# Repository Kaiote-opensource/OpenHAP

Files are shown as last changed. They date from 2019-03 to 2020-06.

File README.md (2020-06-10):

# OpenHAP
A low cost, opensource research tool with remote measurement capability for non invasive, stationary monitoring of household air pollution.



---

OpenHAP gif
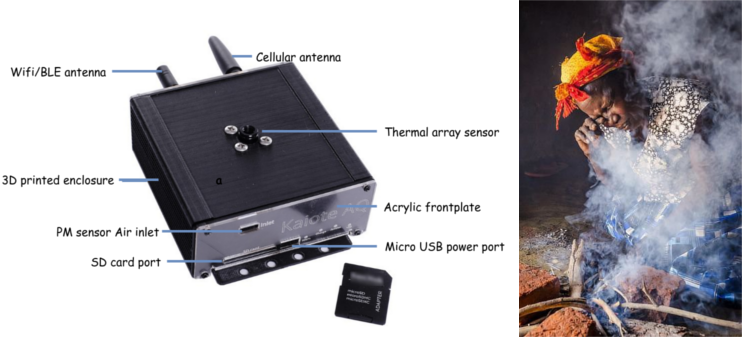
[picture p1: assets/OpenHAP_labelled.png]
OpenHAP image


General parameters monitored include: 

* **Household air pollution** using either PM 1/2.5/10 as pollution indicators.

* **Stove temperatures** in order to attribute pollution measurements above to stove characteristics while in use to answer questions such as - What phase of stove use is pollution highest for a given stove type?

* **Associated human behavioral patterns.** This is to infer behaviour that may have an indirect contribution to pollution. The device infers this by processing wireless beacons emitted by bluetooth wrist straps worn by the members of the household under study. This allows monitoring behaviour and exposure of upto 20 individuals in the same household.

OpenHAP is designed as a modular software/firmware layer that supports customizable measurement hardware. It utilises open datalogging file formats such as:

* **.csv** for timestamped measurement data.

OpenHAP gif

Figure: Sample 2D thermal image(32x24 pixels) of a human being during testing. Temperature is shown on the Z axis on the GIF. Thermal images are used to correlate stove temperature to Particulate measurements. Stove temperature can be well inferred from our tests if the stove is within the sensor's field of view. See graphical plots below from two households chosen from Kibera and rural Kenya(Kiambu).

# Sample results
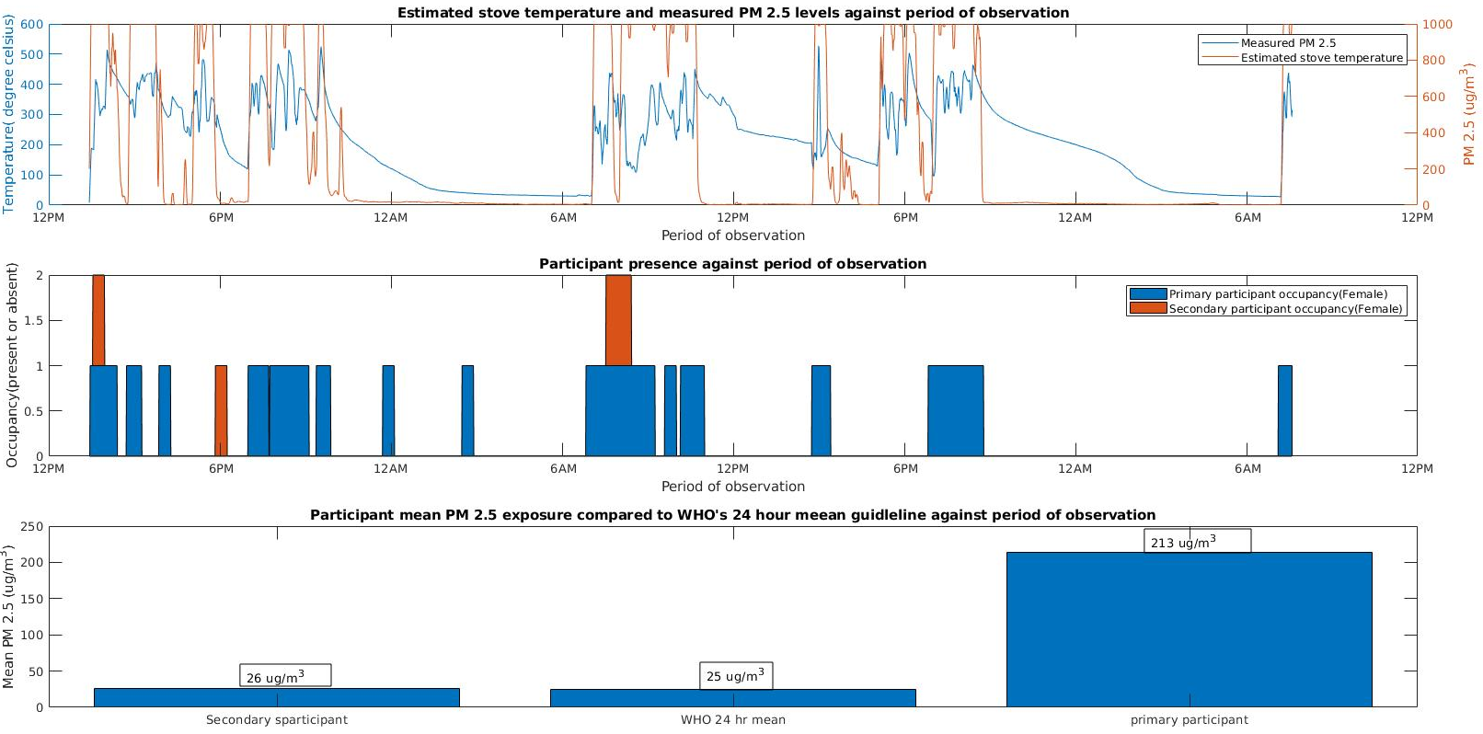
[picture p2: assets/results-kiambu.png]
OpenHAP results kiambu

Measurement results for a rural low income household,Kiambu Kenya with two middle aged women. Household energy use - Three Stone Open Fire(TSOF)

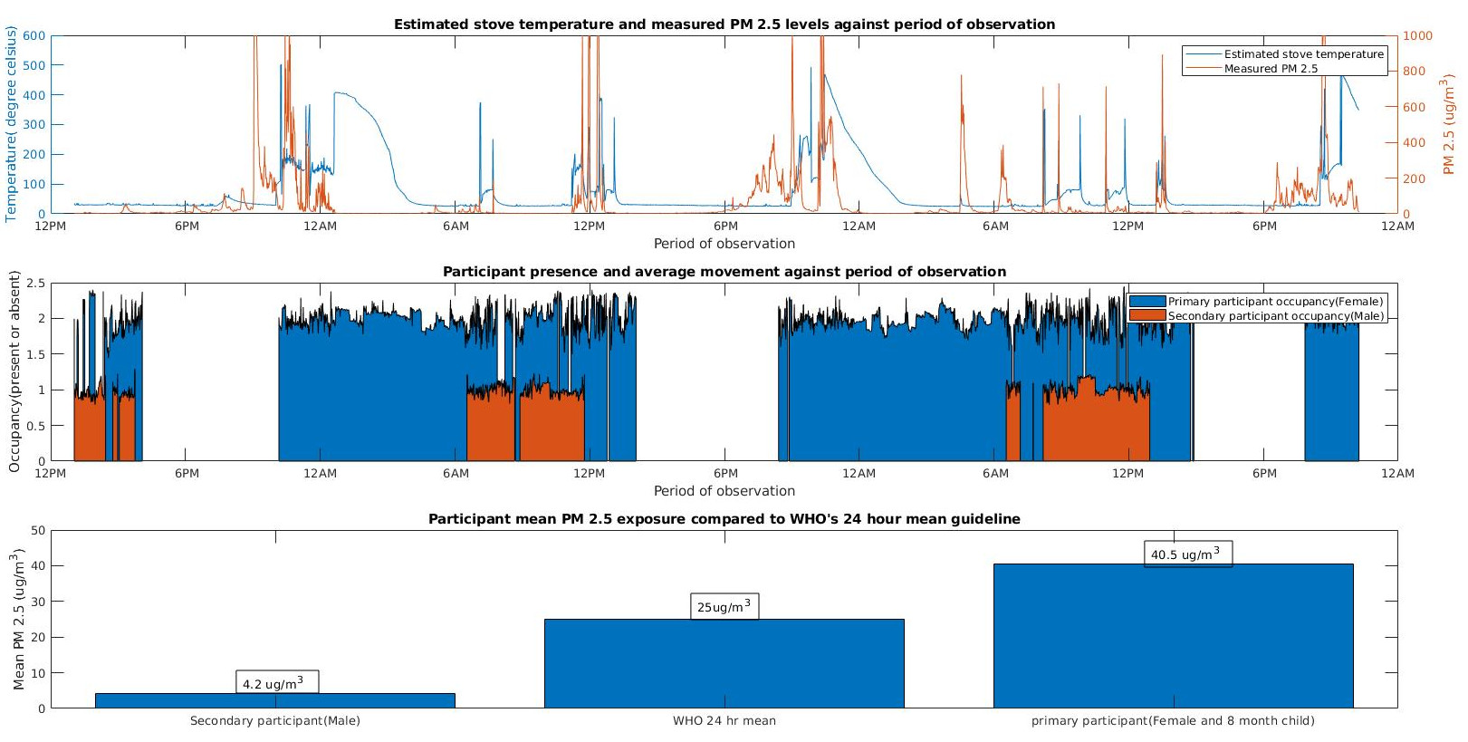
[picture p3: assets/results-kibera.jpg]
OpenHAP results kibera

Measurement results for an urban low income household,Kibera Kenya occupied by a man, wife and 2 children. Children were not monitored in our study as majority of their time was spent with the mother. Household energy use - Kerosene and charcoal briquettes.

# Documentation
OpenHAP's story is covered in [this hackaday article](https://hackaday.com/2019/09/24/fighting-household-air-pollution/) with indepth technical documentation at [this link](https://hackaday.io/project/166510-openhap)

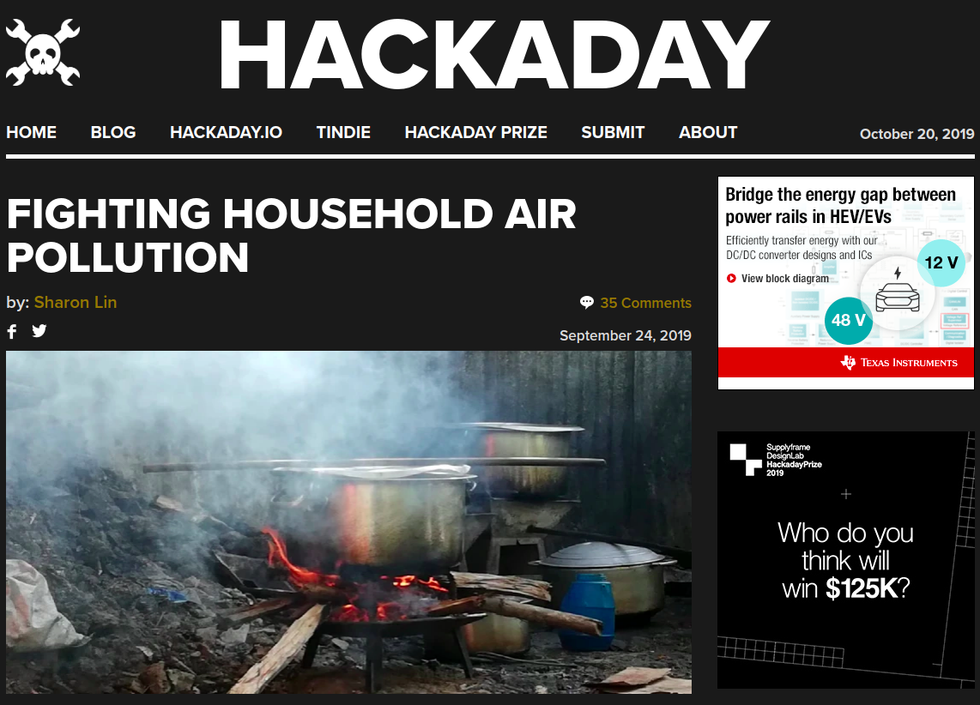
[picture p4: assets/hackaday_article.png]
OpenHAP article (https://hackaday.com/2019/09/24/fighting-household-air-pollution/)


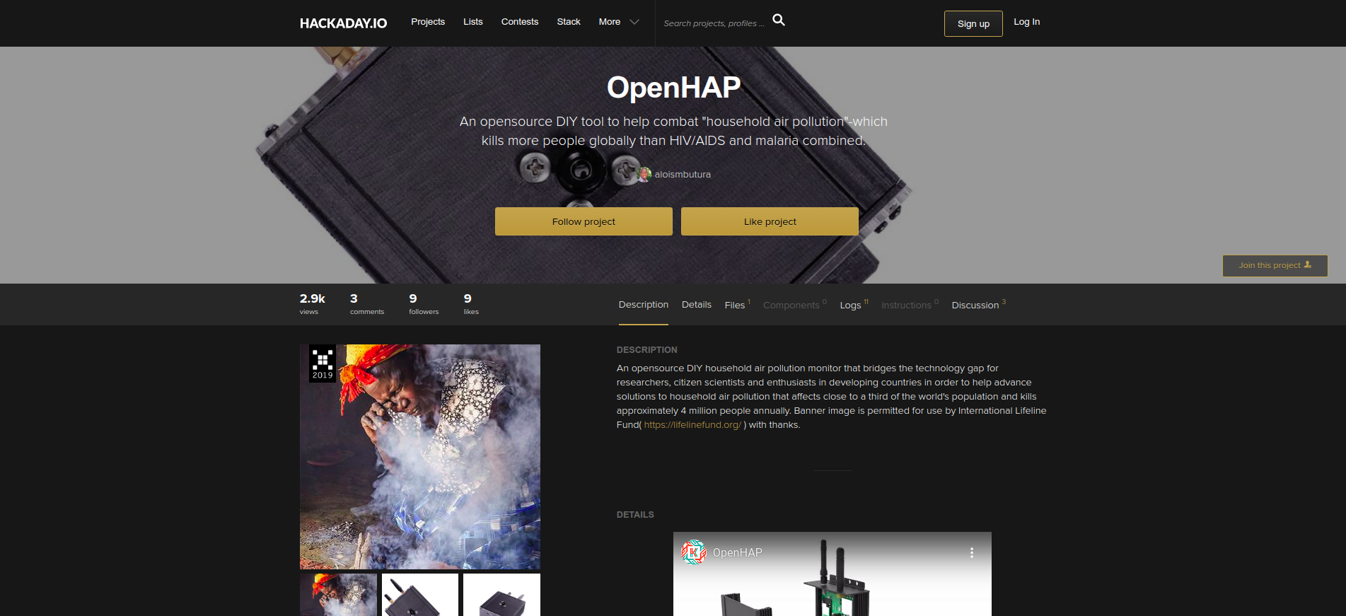
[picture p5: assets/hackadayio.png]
OpenHAP documentation (https://hackaday.io/project/166510-openhap)


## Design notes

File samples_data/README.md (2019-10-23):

# Samples

Real world data captured by OpenHAP and associated simple data analysis examples.

## CSV data fields

* **Time**- Absolute time of measurement in Unix time(Elapsed time in seconds since the unix epoch 00:00:00 UTC - 1 January 1970). A good tool to decode this non-programatically is https://www.epochconverter.com/.

* **Mean temp**- Mean of all 24x32 pixel temperatures in OpenHAP's thermal imager's field of view(FOV).

* **Max temp**- Maximum of all 24x32 pixel infared temperatures in OpenHAP's thermal imager's field of view(FOV).

* **Min temp**- Minimum of all 24x32 pixel temperatures in OpenHAP's thermal imager's field of view(FOV).

* **Temp variance**- Variance of all 24x32 pixel temperatures in OpenHAP's thermal imager's  field of view(FOV).

* **Temp variance**- square root of the Temperature variance above.

* **Humidity**- Ambient humidity at the time of measurement.

* **Temperature**- Ambient temperature at the time of measurement.

* **PM 1**- Amount of PM 1 measured within a one second interval based on the particulate matter sensor's active pump characteristics such volume of air swept per unit time.

* **PM 2.5**- Amount of PM 2.5 measured within a one second interval based on the particulate matter sensor's active pump characteristics such volume of air swept per unit time.

* **PM 10**- Amount of PM 10 measured within a one second interval based on the particulate matter sensor's active pump characteristics such volume of air swept per unit time.

* **Bluetooth tag ID_count**- Number of pings a specific bluetooth tag, identified by its MAC address, makes to an OpenHAP unit within a measurement period.

* **Bluetooth tag ID_mean_dBm**- Average signal streangth in decibel-milliWatts(dBm) of all pings received from a specific bluetooth tag, within a measurement period.

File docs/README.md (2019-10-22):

# Documentation

* **research_papers**- Open research papers on metrology, instrumentation and calibration of low cost sensors, with their citations.

* **datasheets_and_technical_references** - datasheets that guide driver development in the OpenHAP ecosystem. Only drivers of components that have been added or shall be added should have their datasheets here.

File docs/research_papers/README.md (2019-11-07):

# Citations

## Basics

* Schulze, F., Gao, X., Virzonis, D., Damiati, S., Schneider, M. R., & Kodzius, R. (2017). Air Quality Effects on Human Health and Approaches for Its Assessment through Microfluidic Chips. Genes, 8(10), 244. doi:10.3390/genes8100244

## Low cost sensors - Evaluation

* Zheng, Tongshu & Bergin, Michael & Johnson, Karoline & Tripathi, Sachchida & Shirodkar, Shilpa & Landis, Matthew & Sutaria, Ronak & Carlson, David. (2018). Field evaluation of low-cost particulate matter sensors in high- and low-concentration environments. Atmospheric Measurement Techniques. 11. 4823-4846. 10.5194/amt-11-4823-2018. 

* Aerosol Physics and Instrumentation Volume: 19 | Issue: 1 | Pages: 181-194 DOI: 10.4209/aaqr.2017.12.0611

## Ventilation measurements - Tracer Decay technique

* Clito Afonso, Tracer gas technique for measurement of air infiltration and natural ventilation: case studies and new devices for measurement of mechanical air ventilation in ducts, International Journal of Low-Carbon Technologies, Volume 10, Issue 3, September 2015, Pages 188–204, https://doi.org/10.1093/ijlct/ctt025

## Outdoor-Indoor pollution parameter correlation

* Mahmoud M. M. Abdel-Salam (2015) Investigation of PM2.5 and carbon dioxide levels in urban homes, Journal of the Air & Waste Management Association, 65:8, 930-936, DOI: 10.1080/10962247.2015.1040138

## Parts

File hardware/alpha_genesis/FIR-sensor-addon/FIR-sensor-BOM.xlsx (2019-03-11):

C1 | 0.1uF/25V(10%)/0805 | Capacitor_SMD:C_0805_2012Metric_Pad1.15x1.40mm_HandSolder | http://www.yageo.com/documents/recent/UPY-GPHC_X7R_6.3V-to-50V_18.pdf | 311-1141-1-ND | digikey | 1
C2 | 1uF/6.3v(10%)/0805 | Capacitor_SMD:C_0805_2012Metric_Pad1.15x1.40mm_HandSolder | http://www.yageo.com/documents/recent/UPY-GPHC_X7R_6.3V-to-50V_18.pdf | 311-3418-1-ND | digikey | 1
J1 | Conn_02x03_Odd_Even | Connector_PinHeader_2.54mm:PinHeader_2x03_P2.54mm_Vertical | https://cdn.amphenol-icc.com/media/wysiwyg/files/drawing/68000.pdf | 609-3263-ND | digikey | 1
U1 | MLX90640 | lib_kaiote:MLX90640 | https://www.mouser.com/datasheet/2/734/MLX90640-Datasheet-Melexis-1324357.pdf | MLX90640ESF-BAB-000-SP-ND | digikey | 1

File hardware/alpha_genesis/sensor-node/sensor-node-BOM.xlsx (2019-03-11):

Reference designator | Customer reference | Digikey part number | vendor | quantity per board
BT1 | Battery_Cell | BAT-HLD-001-ND | digikey | 1
BT2 | Battery_Cell | 455-1749-1-ND | digikey | 1
BZ1 | Buzzer | 433-1028-ND | digikey | 1
C2, C14 | 1nF/50v(10%)/0805 | 399-1147-1-ND | digikey | 2
C3 | 100uF/6.3v(20%)/1206 | 490-7217-1-ND | digikey | 1
C4 | 1uF/6.3v(10%)/0805 | 311-3418-1-ND | digikey | 1
C6 - C10 | 10uF/25V(10%)/0805 | 490-5523-1-ND | digikey | 4
C8 | 220uF/tantalum | 478-6612-1-ND | digikey | 1
C1 - C19 | 0.1uF/25V(10%)/0805 | 311-1141-1-ND | digikey | 7
C15, C16 | 4.7uF/16v/10%/0805 | CL21A475KOFNNNE | digikey | 2
C17 | 220nF/50V(10%)/0805 | 587-1287-1-ND | digikey | 1
D1, D19 | TVS_5V | SMAJ5.0ALFCT-ND | digikey | 2
D2 - D17 | D_Schottky | B120-FDICT-ND | digikey | 3
D3 - D8 | CDSOT23-T03C | CDSOT23-T03CCT-ND | digikey | 6
D9 - D16 | TVS_3V3 | SMBJ3V3-E3/52GITR-ND | digikey | 4
D11 | Red/RA | 754-1840-1-ND | digikey | 1
D13 - D24 | Green/RA | 754-1057-1-ND | digikey | 3
J1 | USB_B_Micro | WM17141CT-ND | digikey | 1
J2 | TE_2041021 | A101492CT-ND | digikey | 1
J3 | Conn_02x03_Odd_Even | 609-3263-ND | digikey | 1
J4 | Conn_01x07 | S5443-ND | digikey | 1
J5 | Conn_01x03_Male | 732-5316-ND | digikey | 1
J6 | Conn_01x08 | WM7612CT-ND | digikey | 1
Q1, Q2 | S8050 | MMSS8050-H-TPMSCT-ND | digikey | 2
Q3, Q9 | SI2323DDS-T1-GE3 | SI2323DDS-T1-GE3 | digikey | 2
Q4 - Q8 | BSS138 | BSS138CT-ND | digikey | 4
R12, R13 | 12k(1%) | A126337CT-ND | digikey | 2
R1 - R28 | 10k(5%) | 311-10KARCT-ND | digikey | 16
R15 - R29 | 10k(0.5%) | RR12P10.0KDCT-ND | digikey | 3
R18, R31 | 100k(5%) | RMCF0805FT100KCT-ND | digikey | 2
R19, R20 | 470R(5%) | P470ACT-ND | digikey | 2
R21, R22 | 2.4k(5%) | RMCF0805JT2K40CT-ND | digikey | 2
R23, R27 | 2K(5%) | RMCF0805JT2K00CT-ND | digikey | 2
R30 | 2.4k(0.1%) | P2.4KDACT-ND | digikey | 1
SW1 | ~ | EG2508-ND | digikey | 1
TP1 - TP14 | ~ | 36-5015CT-ND | digikey | 14
U1 | DS3231SN | DS3231SN#T&RCT-ND | digikey | 1
U2 | MIKROE_CLICK_GSM | 1471-1065-ND | digikey | 1
U3 | ESP32-WROVER | 1904-1017-1-ND | digikey | 1
U4 | TCA9534 | 296-40573-1-ND | digikey | 1
U5 | NCP1117-3.3_SOT223 | NCP1117ST33T3GOSCT-ND | digikey | 1
U7 | 74LVC1G3157 | 296-14908-1-ND | digikey | 1
U8 | MCP73812T-420I-OT | MCP73832T-2ACI/OTCT-ND | digikey | 1
U9 | HIH6030-021-001 | 480-5704-1-ND | digikey | 1

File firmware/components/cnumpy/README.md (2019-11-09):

# cnumpy

cnumpy is a derivative work of c2numpy by Jim Pivarski . cnumpy carries over the original Apache licence used.

cnumpy is an ANSI C compatible library that allows the ability to read and write .npy files. npz files are not supported as they use gzip compression which only supports block compression(deflate/infalte operations must have a destination buffer in RAM, limiting performance on large file operations. This would make it unable to support low ram utilisation operations.

# file format

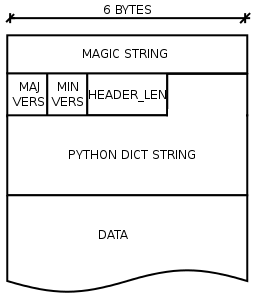
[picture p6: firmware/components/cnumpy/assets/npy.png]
npy file


The .npy file format can be found here: https://numpy.org/devdocs/reference/generated/numpy.lib.format.html

# OpenHAP application

The npy file format is useful for storing thermal image data. It may also be extended to other data types with fixed/pre-determined size.

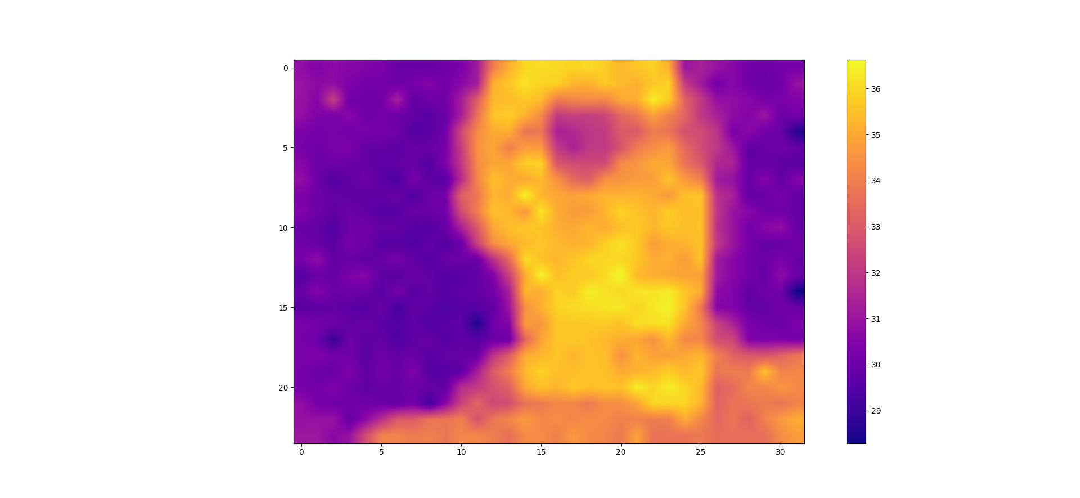
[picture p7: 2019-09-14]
firmware/components/drivers_thermal_imagers/python/Figure_1.png

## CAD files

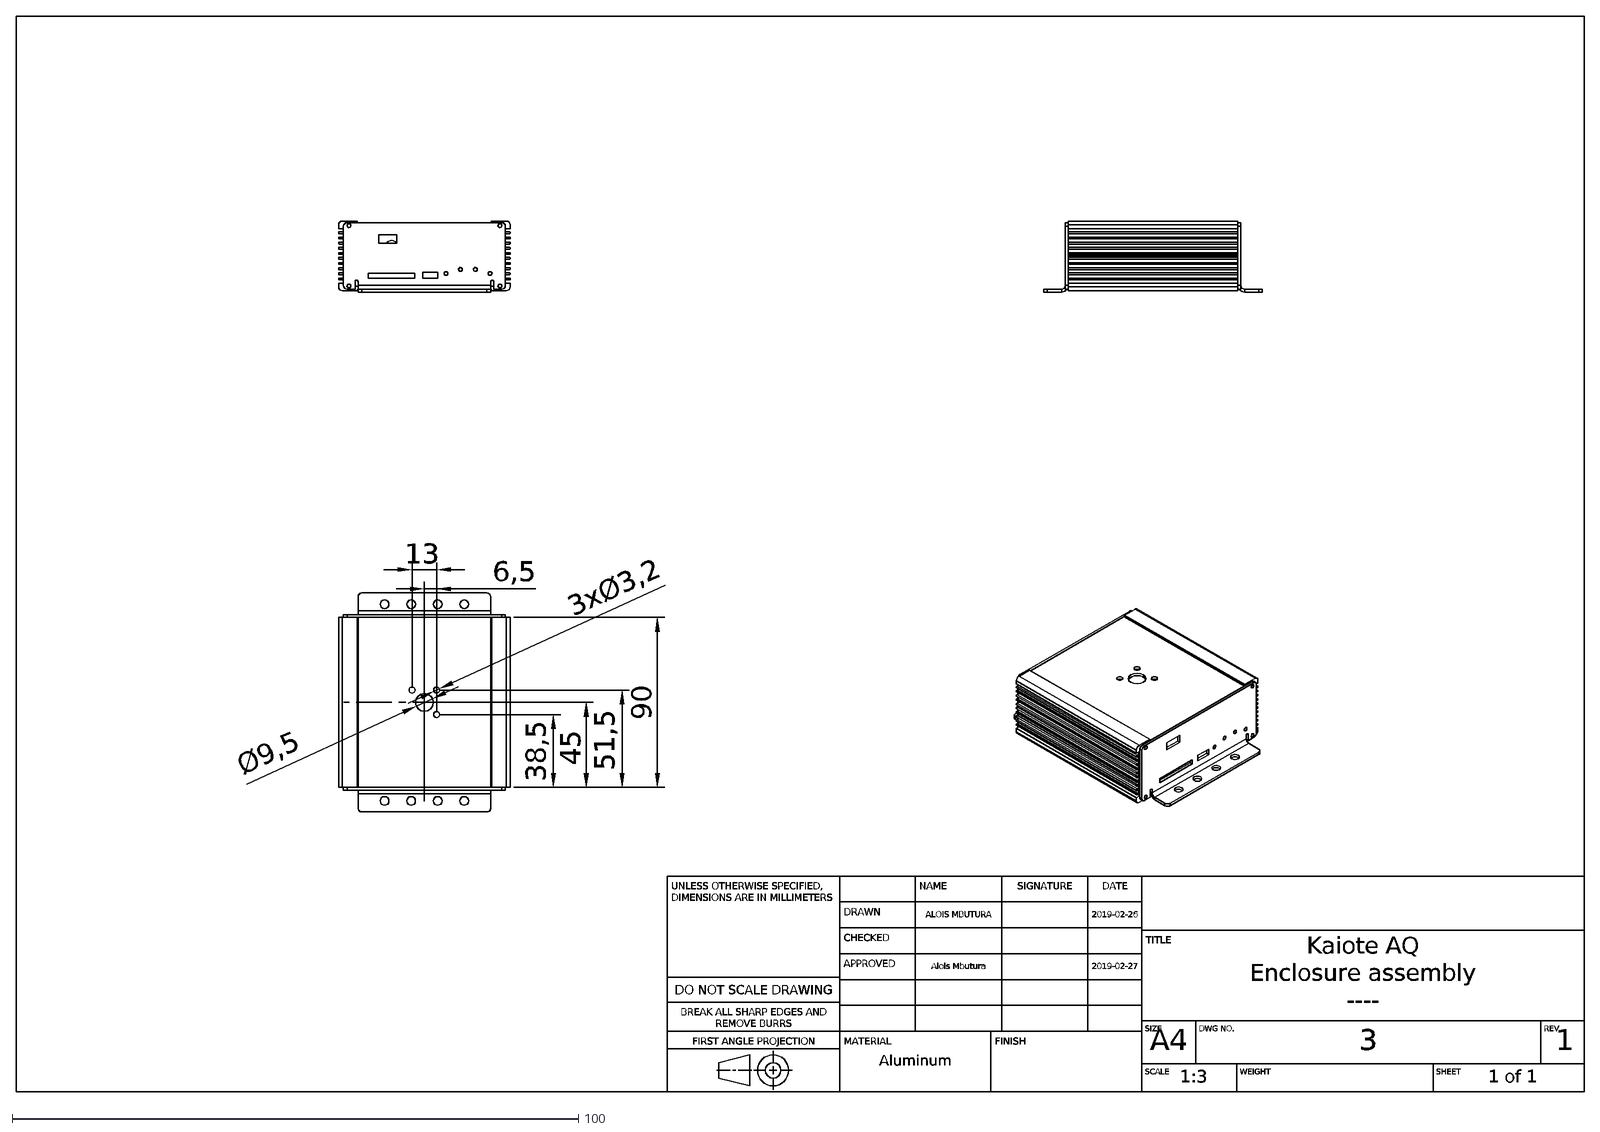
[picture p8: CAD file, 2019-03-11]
hardware/alpha_genesis/MCAD/Enclosure_instructions/Assembly/Enclosure_assembly.dxf
UNLESS OTHERWISE SPECIFIED, DIMENSIONS ARE IN MILLIMETERS
DO NOT SCALE DRAWING
BREAK ALL SHARP EDGES AND REMOVE BURRS
FIRST ANGLE PROJECTION
SIGNATURE
NAME
DATE
DRAWN
ALOIS MBUTURA
2019-02-26
CHECKED
APPROVED
Alois Mbutura
2019-02-27
MATERIAL
Aluminum
FINISH
TITLE
Kaiote AQ
Enclosure assembly
----
SIZE
A4
DWG NO.
3
REV.
1
SCALE
1:3
WEIGHT
SHEET
1 of 1
90
38,5
45
51,5
13
6,5
Ø9,5
3xØ3,2

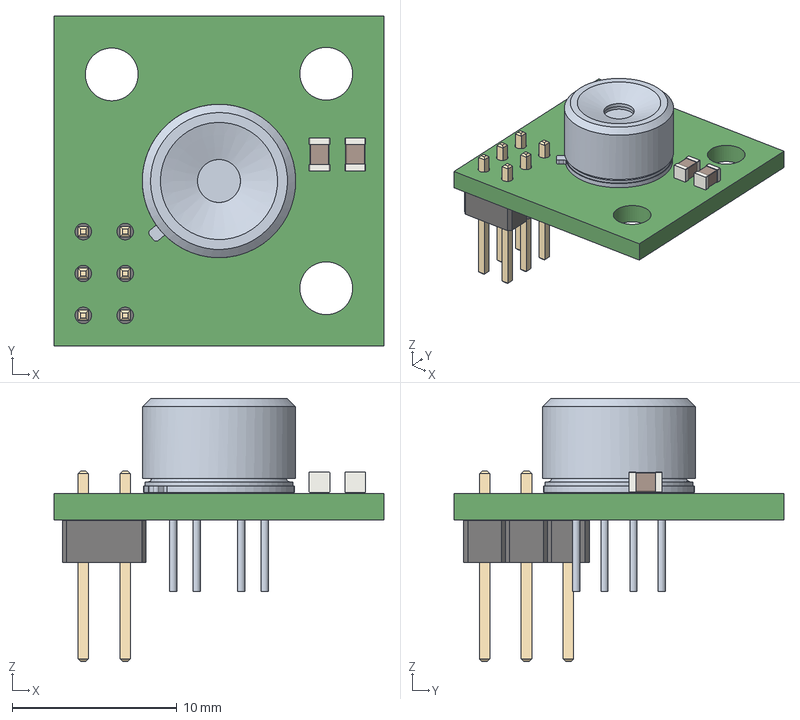
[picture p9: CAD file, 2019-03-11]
hardware/alpha_genesis/FIR-sensor-addon/FIR-sensor-addon.step
20.0 x 20.0 x 15.9 mm

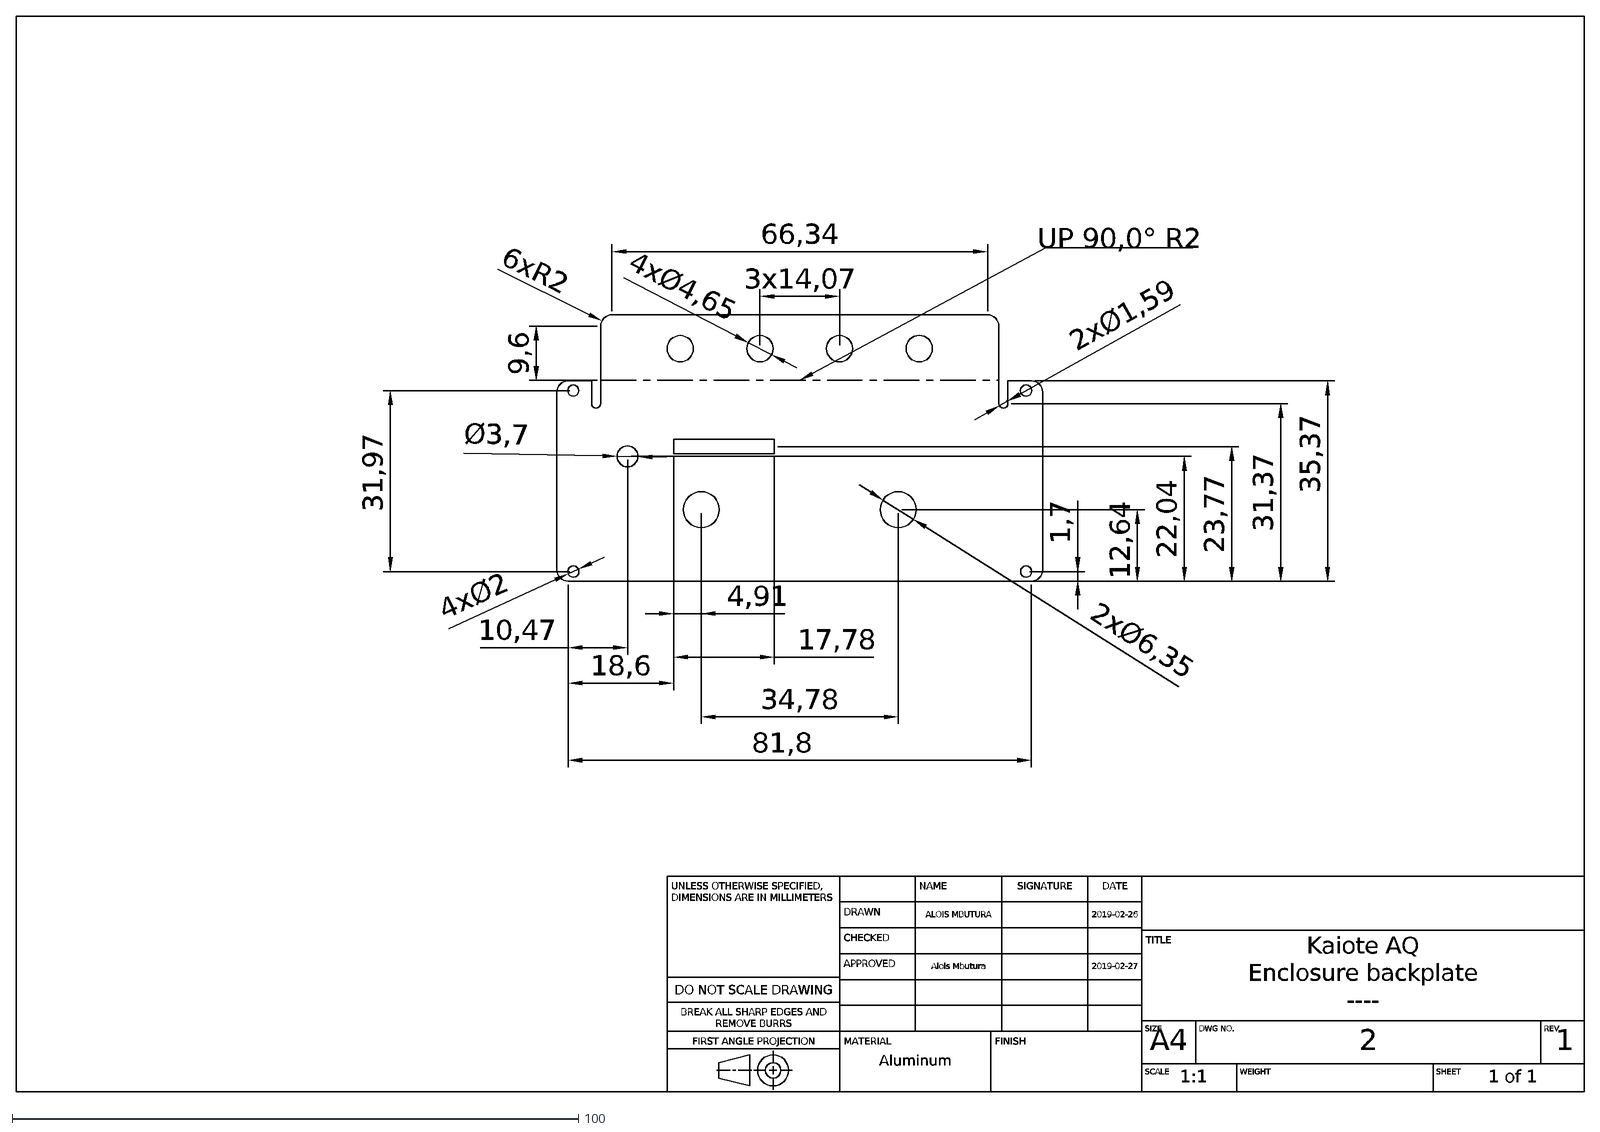
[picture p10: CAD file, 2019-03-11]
hardware/alpha_genesis/MCAD/Enclosure_instructions/backplate/Enclosure_backplate.dxf
UNLESS OTHERWISE SPECIFIED, DIMENSIONS ARE IN MILLIMETERS
DO NOT SCALE DRAWING
BREAK ALL SHARP EDGES AND REMOVE BURRS
FIRST ANGLE PROJECTION
SIGNATURE
NAME
DATE
DRAWN
ALOIS MBUTURA
2019-02-26
CHECKED
APPROVED
Alois Mbutura
2019-02-27
MATERIAL
Aluminum
FINISH
TITLE
Kaiote AQ
Enclosure backplate
----
SIZE
A4
DWG NO.
2
REV.
1
SCALE
1:1
WEIGHT
SHEET
1 of 1
4xØ2
81,8
34,78
1,7
12,64
22,04
23,77
31,37
35,37
2xØ1,59
31,97
9,6
6xR2
66,34
17,78
10,47
2xØ6,35
18,6
4,91
4xØ4,65
3x14,07
Ø3,7
UP 90,0° R2

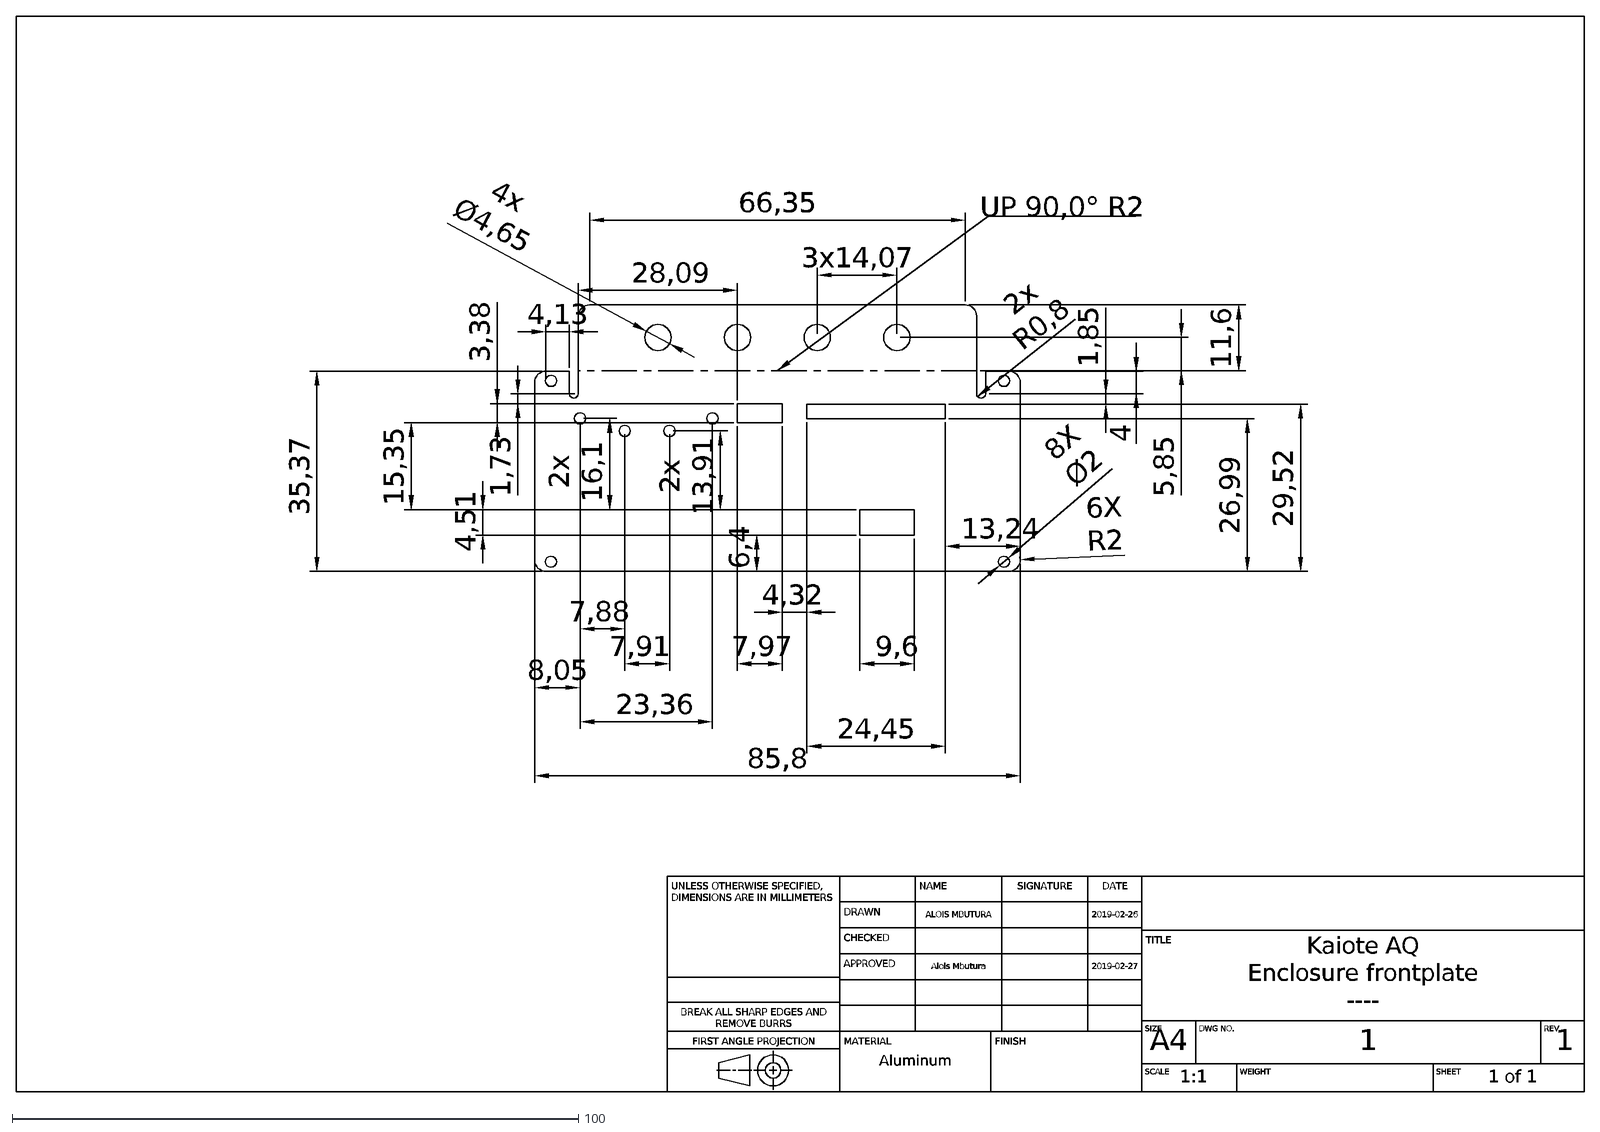
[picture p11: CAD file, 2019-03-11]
hardware/alpha_genesis/MCAD/Enclosure_instructions/frontplate/Enclosure_frontplate.dxf
UNLESS OTHERWISE SPECIFIED, DIMENSIONS ARE IN MILLIMETERS
BREAK ALL SHARP EDGES AND REMOVE BURRS
FIRST ANGLE PROJECTION
SIGNATURE
NAME
DATE
DRAWN
ALOIS MBUTURA
2019-02-26
CHECKED
APPROVED
Alois Mbutura
2019-02-27
MATERIAL
Aluminum
FINISH
TITLE
Kaiote AQ
Enclosure frontplate
----
SIZE
A4
DWG NO.
1
REV.
SCALE
1:1
WEIGHT
SHEET
1 of 1
9,6
24,45
7,97
85,8
8X Ø2
6X R2
3,38
35,37
66,35
4x Ø4,65
11,6
4,51
4
2x R0,8
4,13
5,85
6,4
15,35
26,99
29,52
1,85
28,09
1,73
3x14,07
13,24
2x 13,91
2x 16,1
7,91
23,36
7,88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

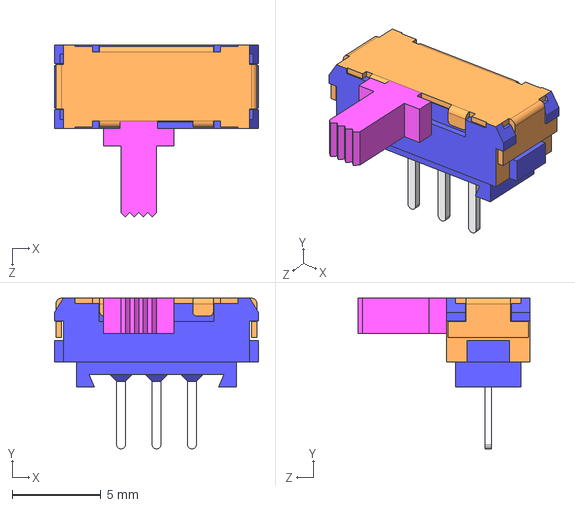
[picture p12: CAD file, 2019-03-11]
hardware/alpha_genesis/MCAD/SSSS916400.STEP
11.5 x 8.50 x 9.70 mm

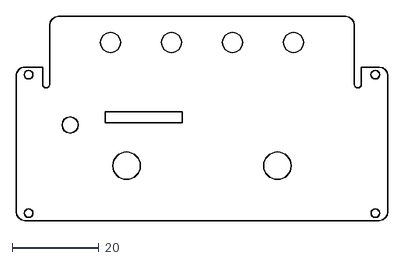
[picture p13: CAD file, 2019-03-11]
hardware/alpha_genesis/MCAD/Enclosure_instructions/backplate/enclosure_backplate_unannoted.dxf
85.8 x 47.1

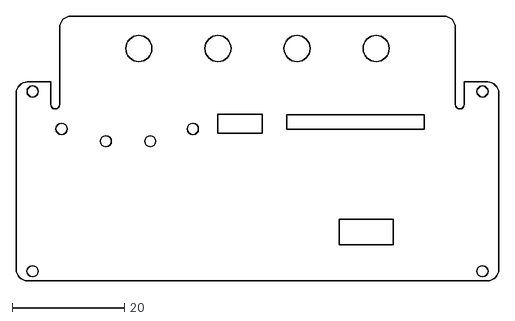
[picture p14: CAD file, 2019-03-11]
hardware/alpha_genesis/MCAD/Enclosure_instructions/frontplate/Enclosure_frontplate_unannoted.dxf
85.8 x 47.1

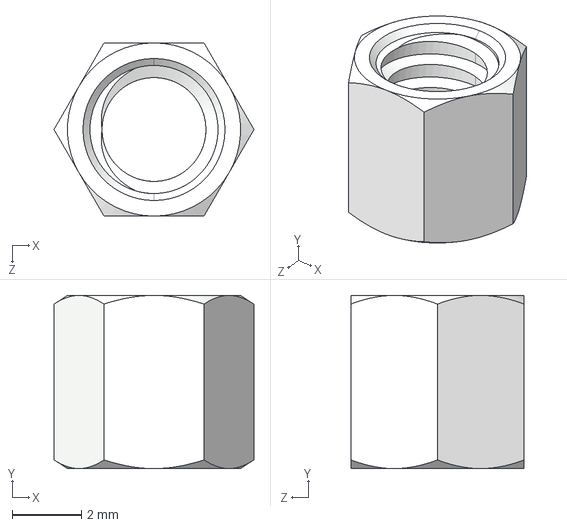
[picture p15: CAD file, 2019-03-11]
hardware/alpha_genesis/MCAD/keystone-PN24430.STEP
5.77 x 5.00 x 5.00 mm

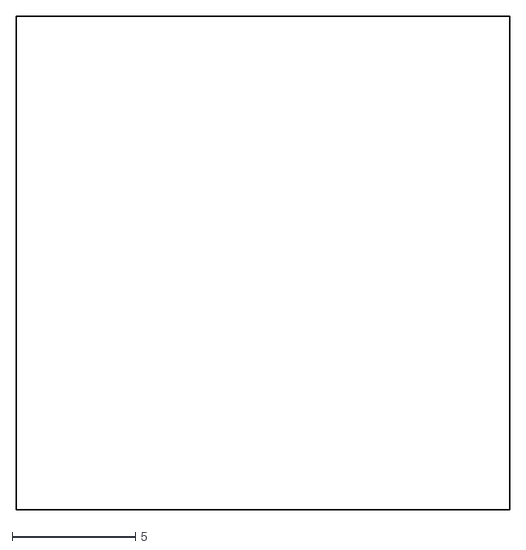
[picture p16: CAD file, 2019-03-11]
hardware/alpha_genesis/MCAD/FIR_sensor_PCB_outline.dxf
20.0 x 20.0

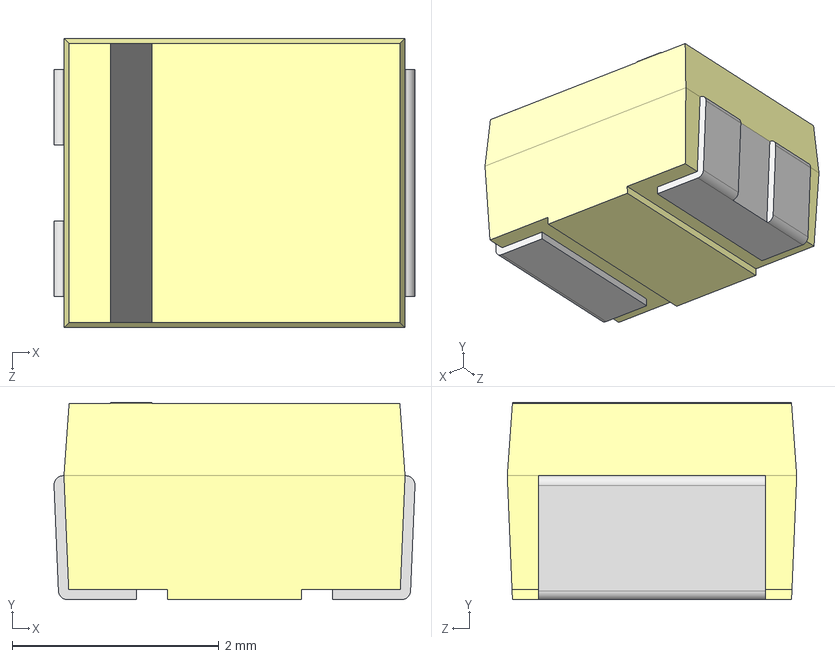
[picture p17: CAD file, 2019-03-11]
hardware/alpha_genesis/MCAD/EIA_1411.step
3.49 x 1.91 x 2.80 mm

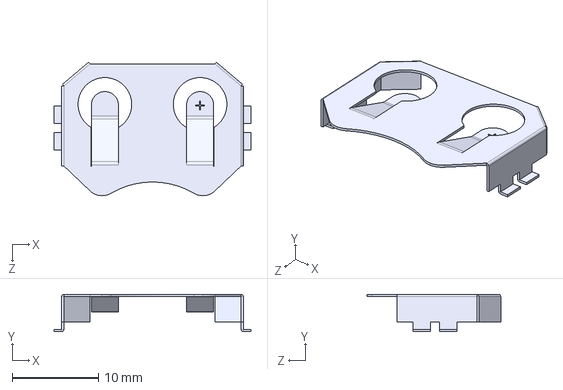
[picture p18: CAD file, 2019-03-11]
hardware/alpha_genesis/MCAD/BAT-HLD-001-TR--3DModel-STEP-56544.STEP
22.9 x 4.32 x 15.5 mm

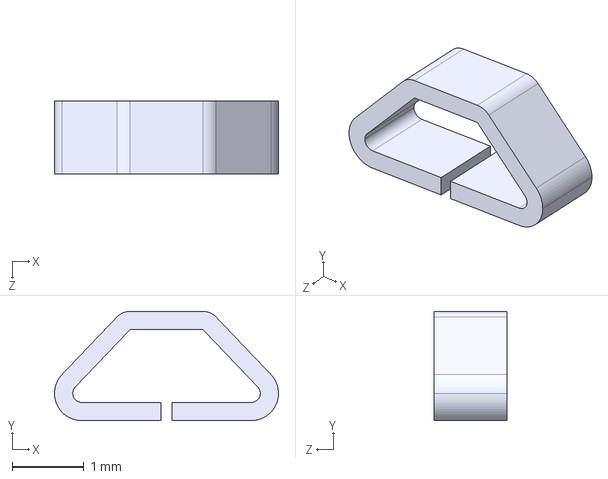
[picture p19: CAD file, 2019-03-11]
hardware/alpha_genesis/MCAD/keystone-PN5015.STEP
3.12 x 1.52 x 1.02 mm

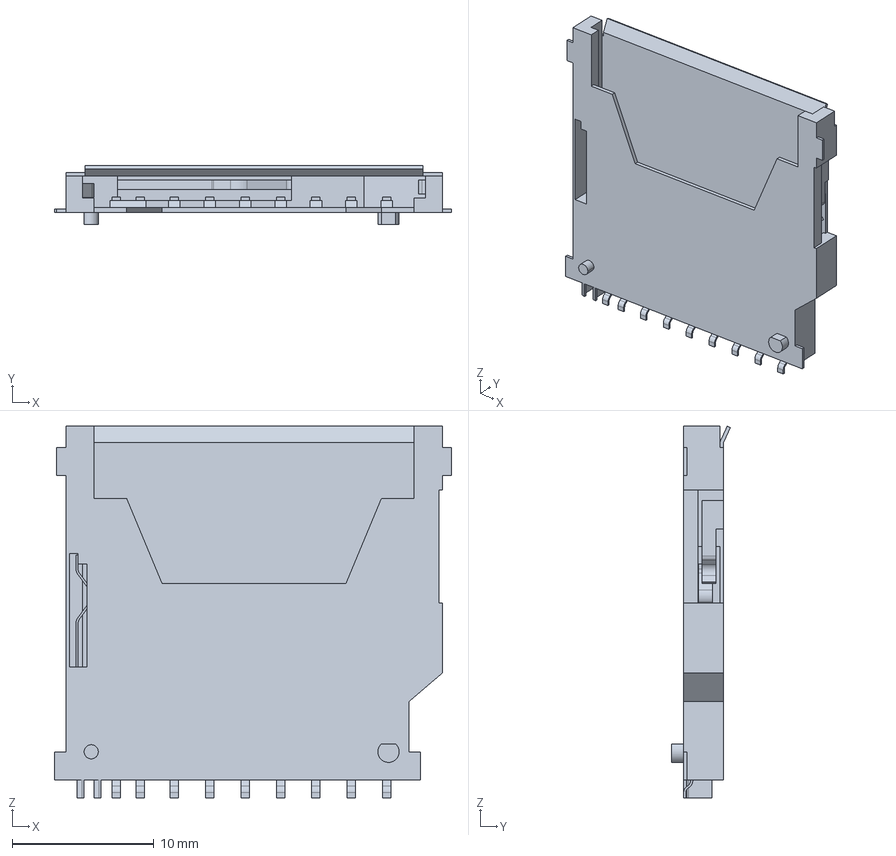
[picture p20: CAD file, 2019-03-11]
hardware/alpha_genesis/MCAD/c-2041021-4-b-3d.stp
28.0 x 4.15 x 26.2 mm

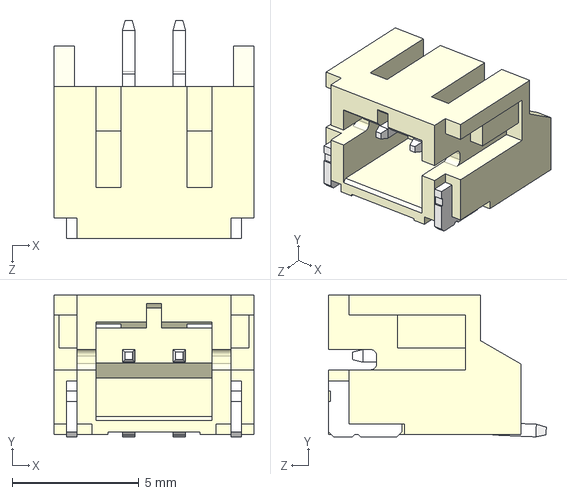
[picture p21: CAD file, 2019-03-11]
hardware/alpha_genesis/MCAD/S2B-PH-SM4-TB(LF)(SN)--3DModel-STEP-56544.STEP
7.90 x 5.60 x 8.60 mm

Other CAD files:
hardware/alpha_genesis/MCAD/TL1105VFxxxx.stp
hardware/alpha_genesis/MCAD/132117rp_3d_model.stp
hardware/alpha_genesis/MCAD/APA2107.STEP
hardware/alpha_genesis/MCAD/APAMBJ-135.STEP
hardware/alpha_genesis/MCAD/APDA1806.STEP
hardware/alpha_genesis/MCAD/MLX90640_120__APERTURE_ANY_ASM.step
hardware/alpha_genesis/MCAD/PCB outline.dxf
hardware/alpha_genesis/MCAD/TR Fastenings Ltd-M3X4MM.step
hardware/alpha_genesis/MCAD/ZH03B.step
hardware/alpha_genesis/MCAD/c-1-1825027-7-g-3d.stp

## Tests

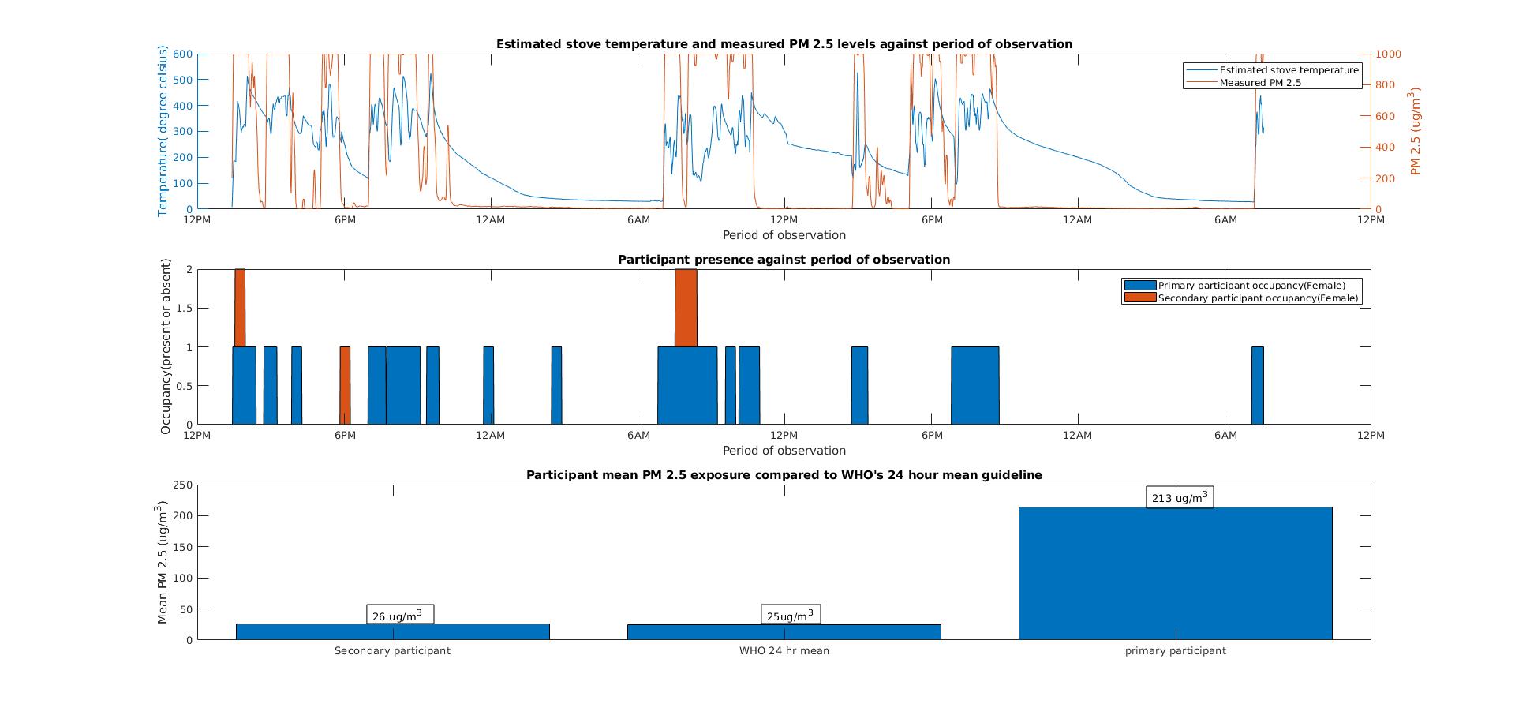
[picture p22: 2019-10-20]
samples_data/analysis_tools/results.jpg

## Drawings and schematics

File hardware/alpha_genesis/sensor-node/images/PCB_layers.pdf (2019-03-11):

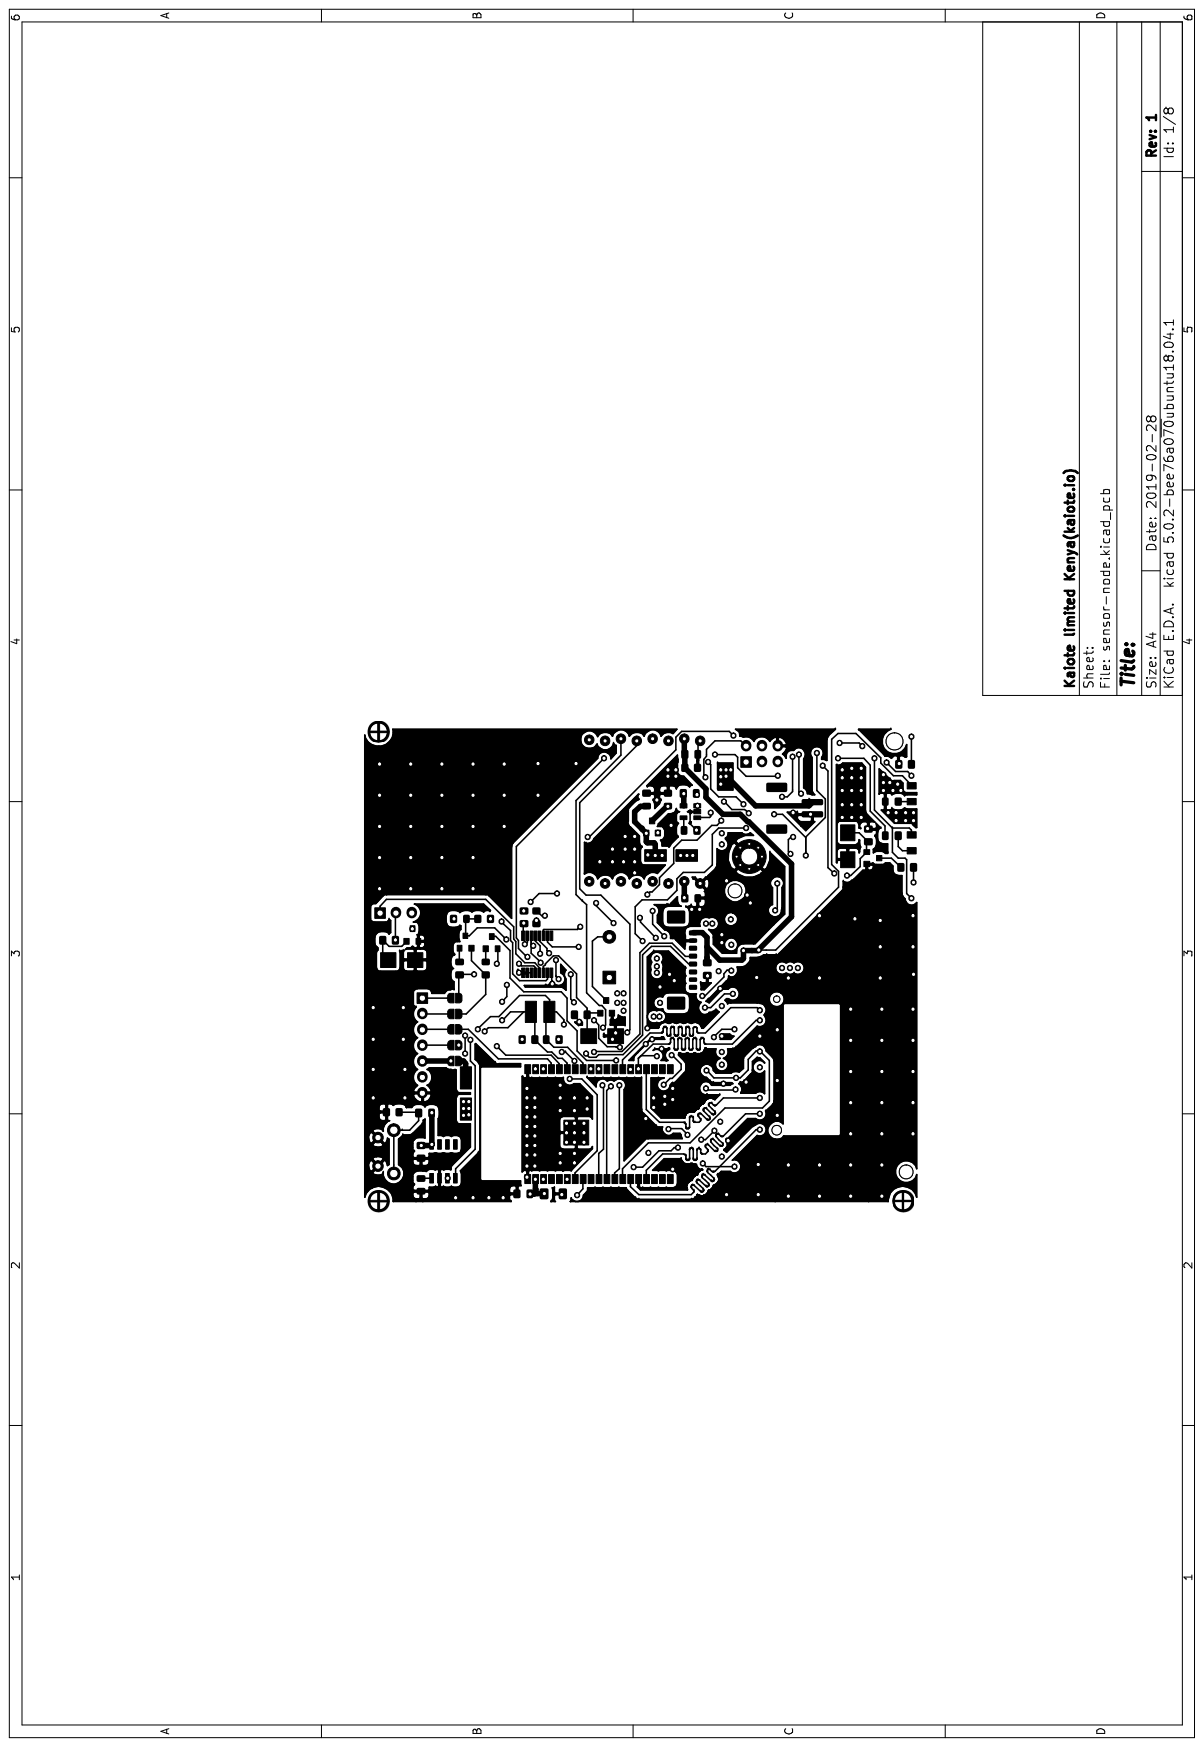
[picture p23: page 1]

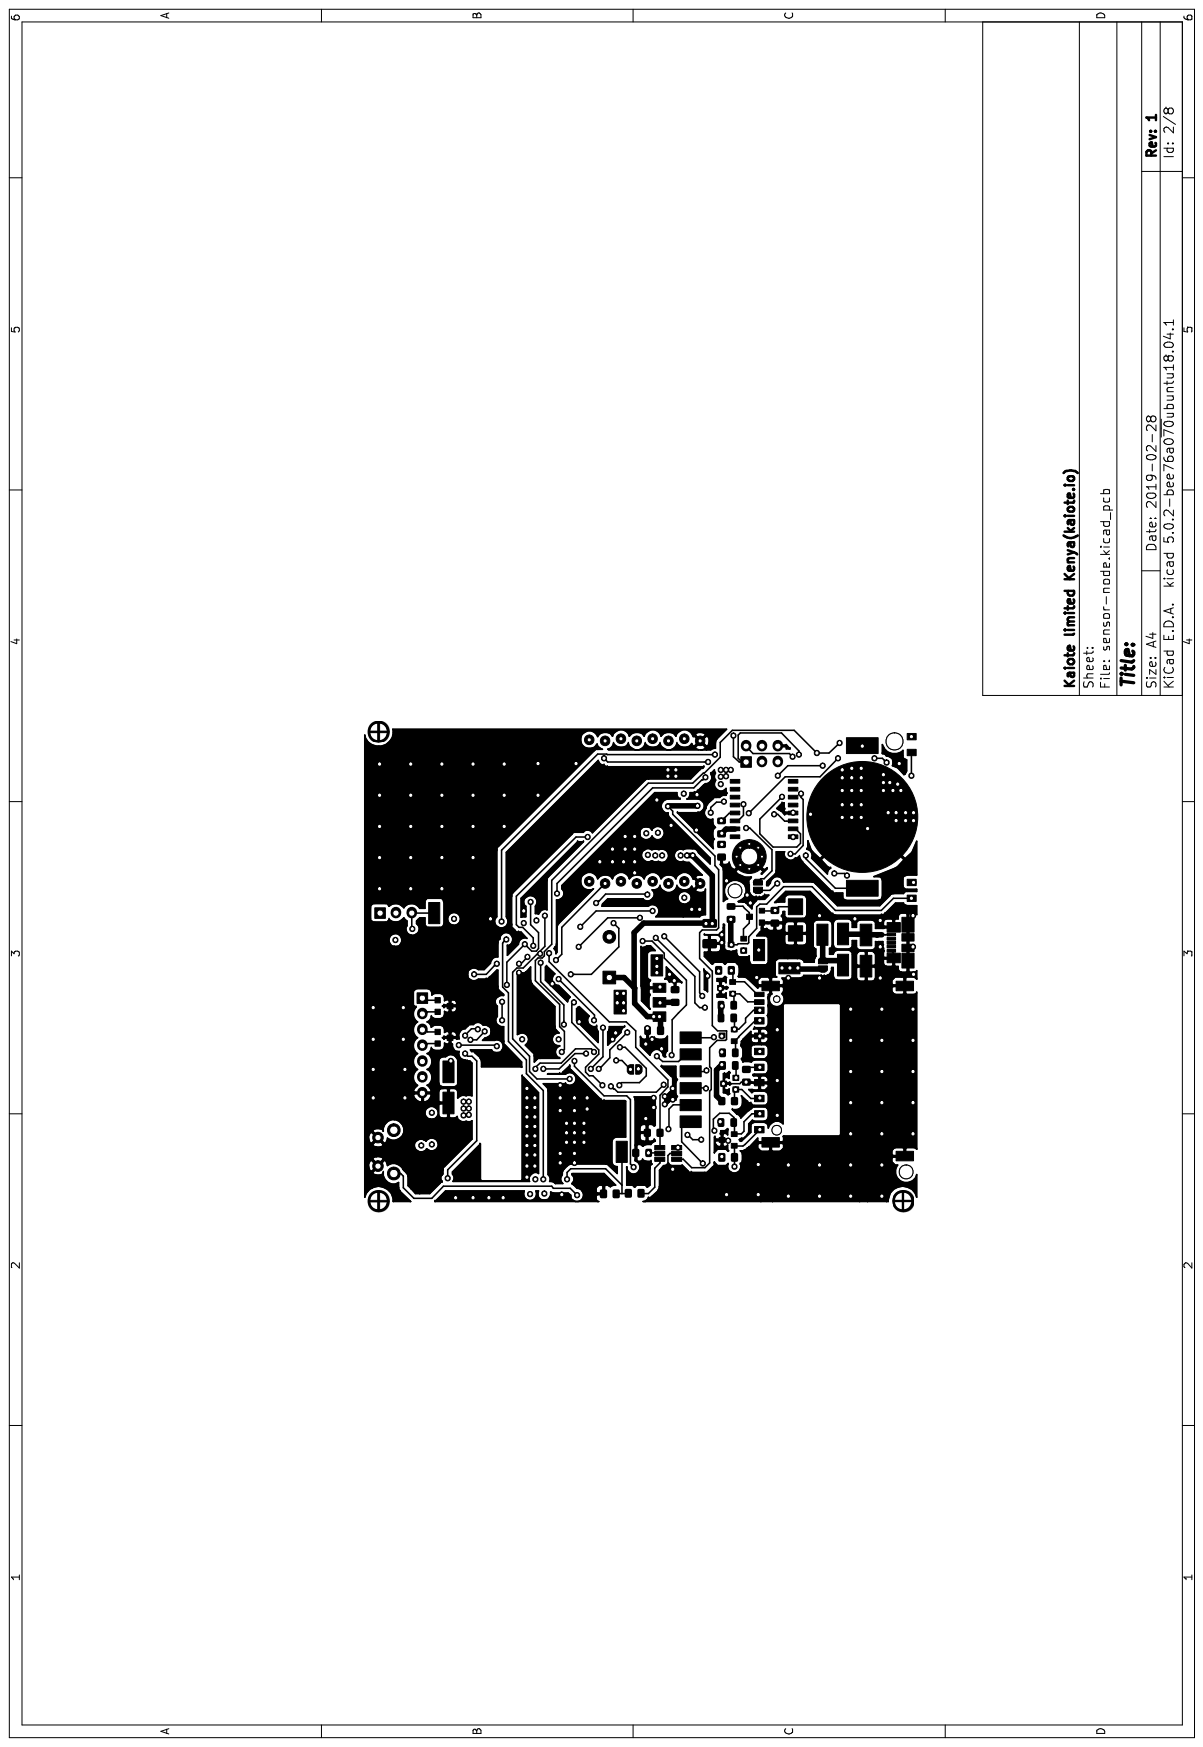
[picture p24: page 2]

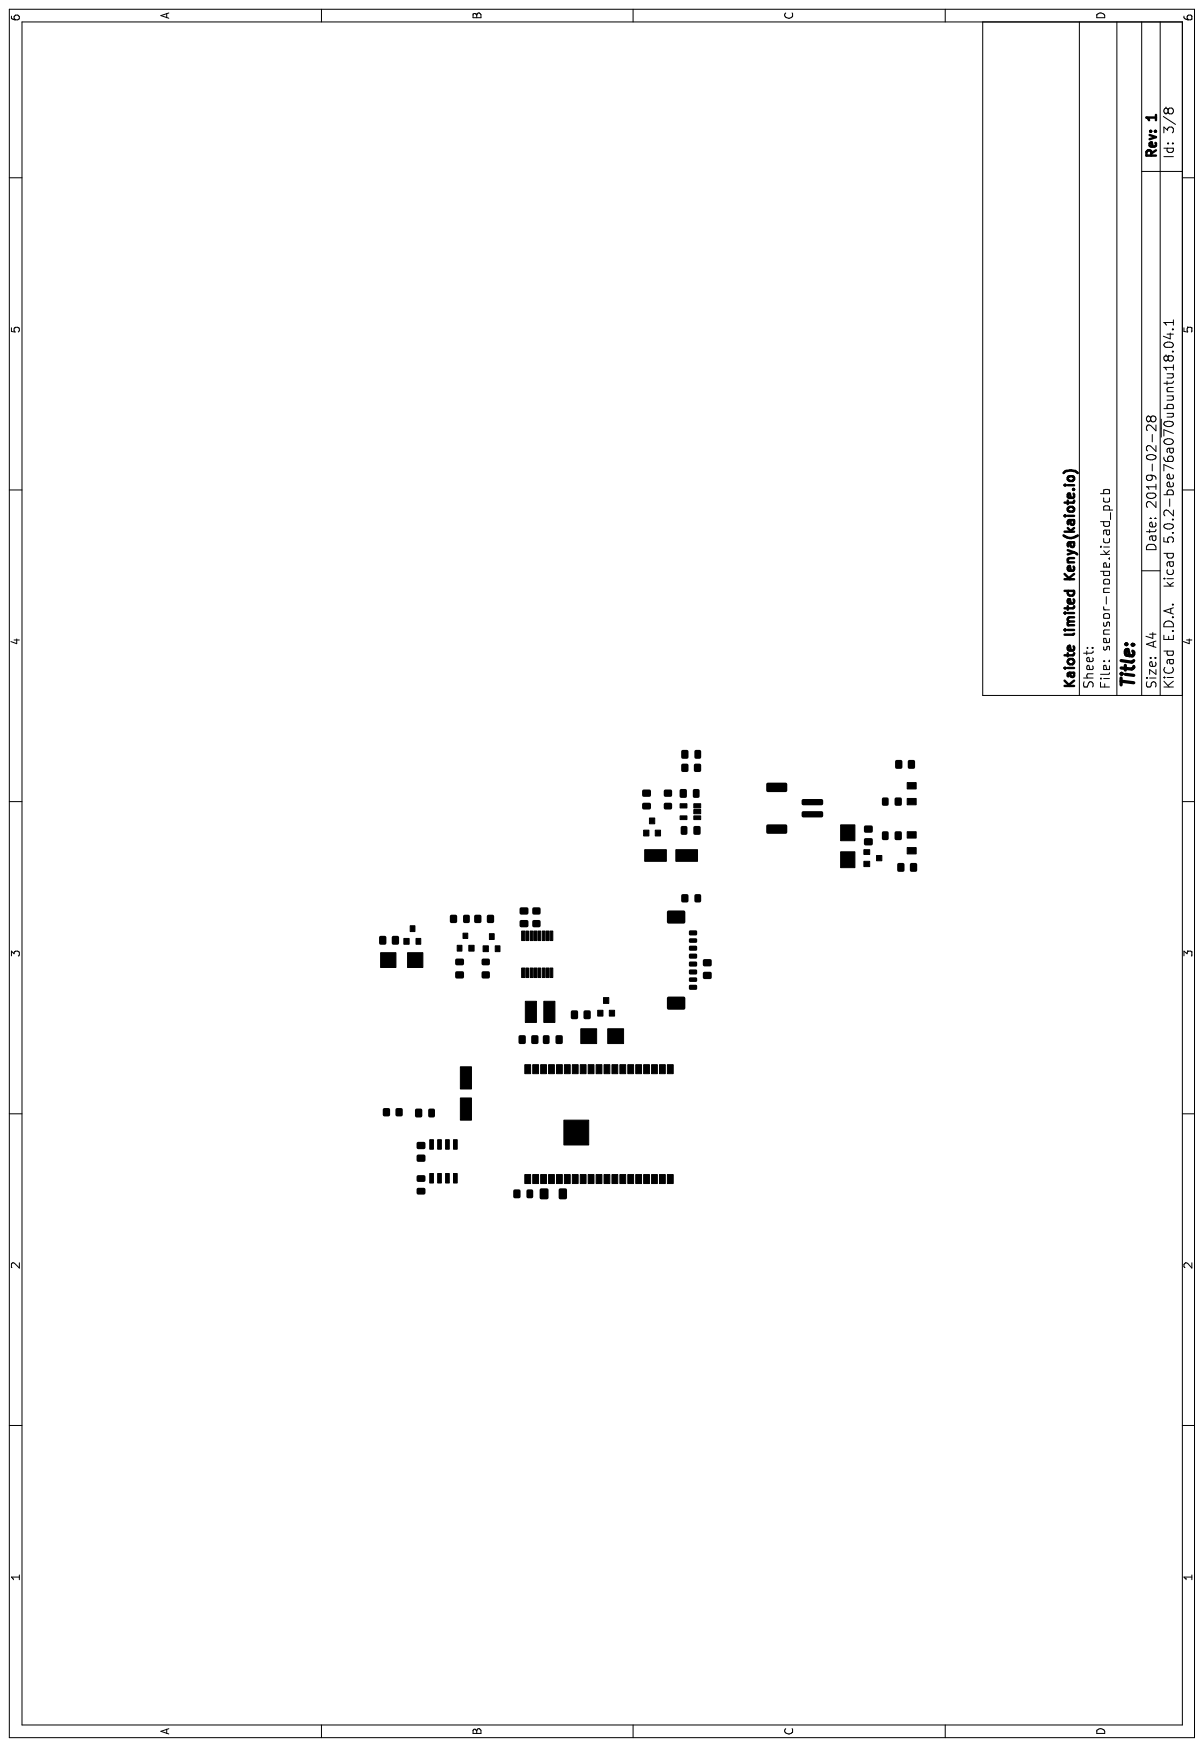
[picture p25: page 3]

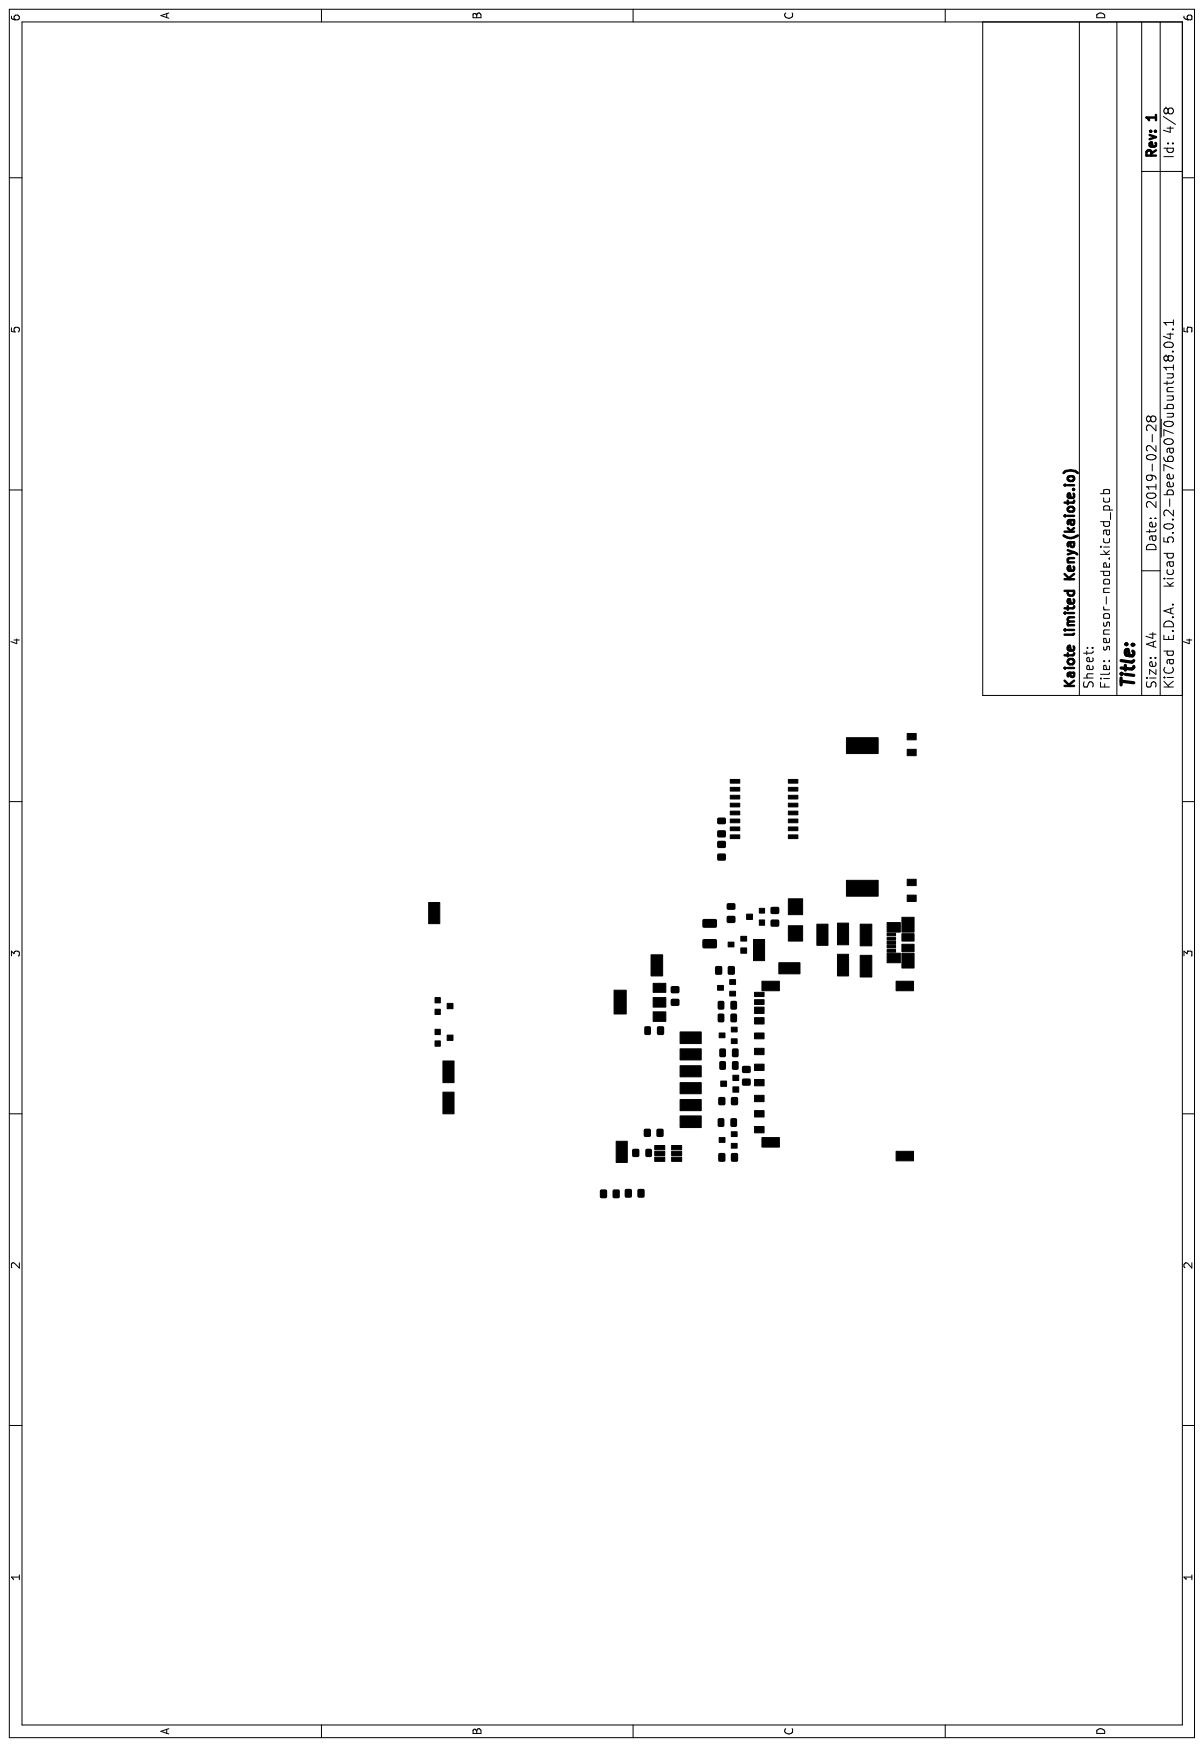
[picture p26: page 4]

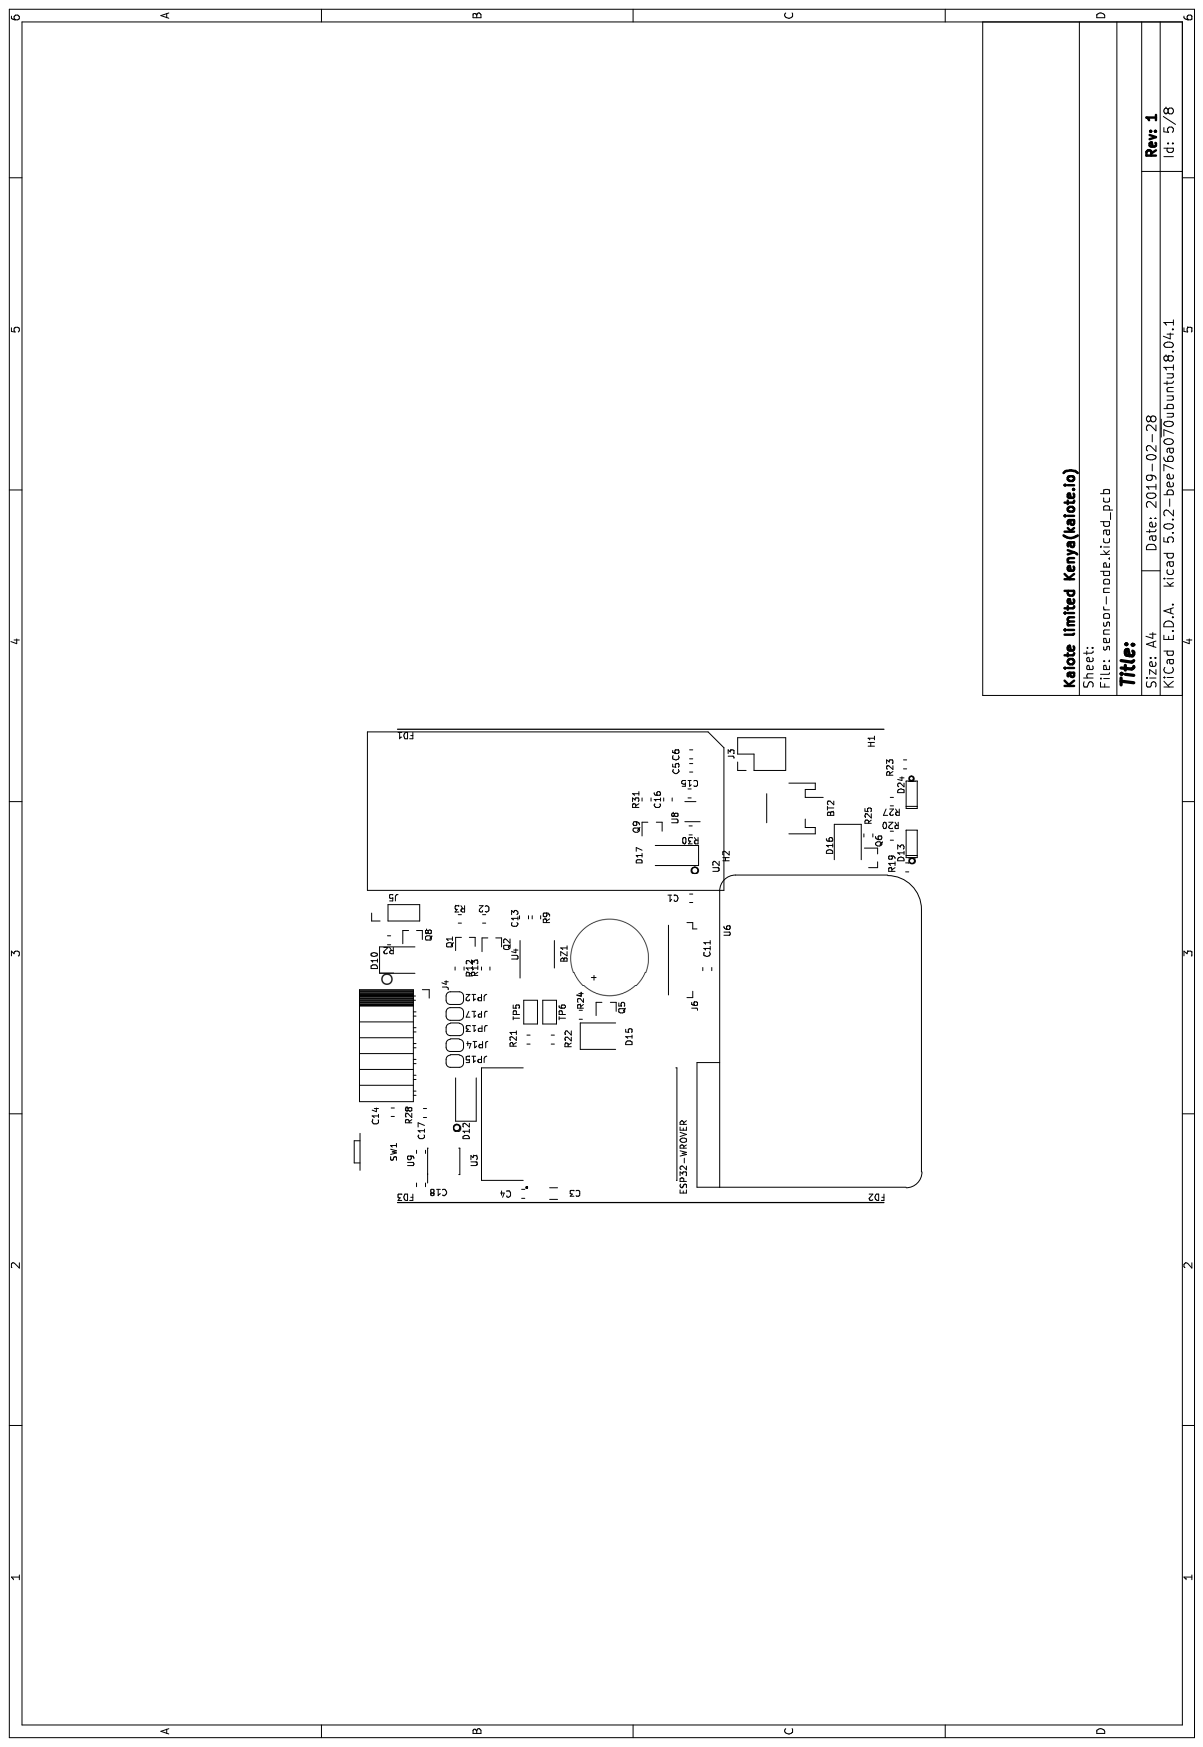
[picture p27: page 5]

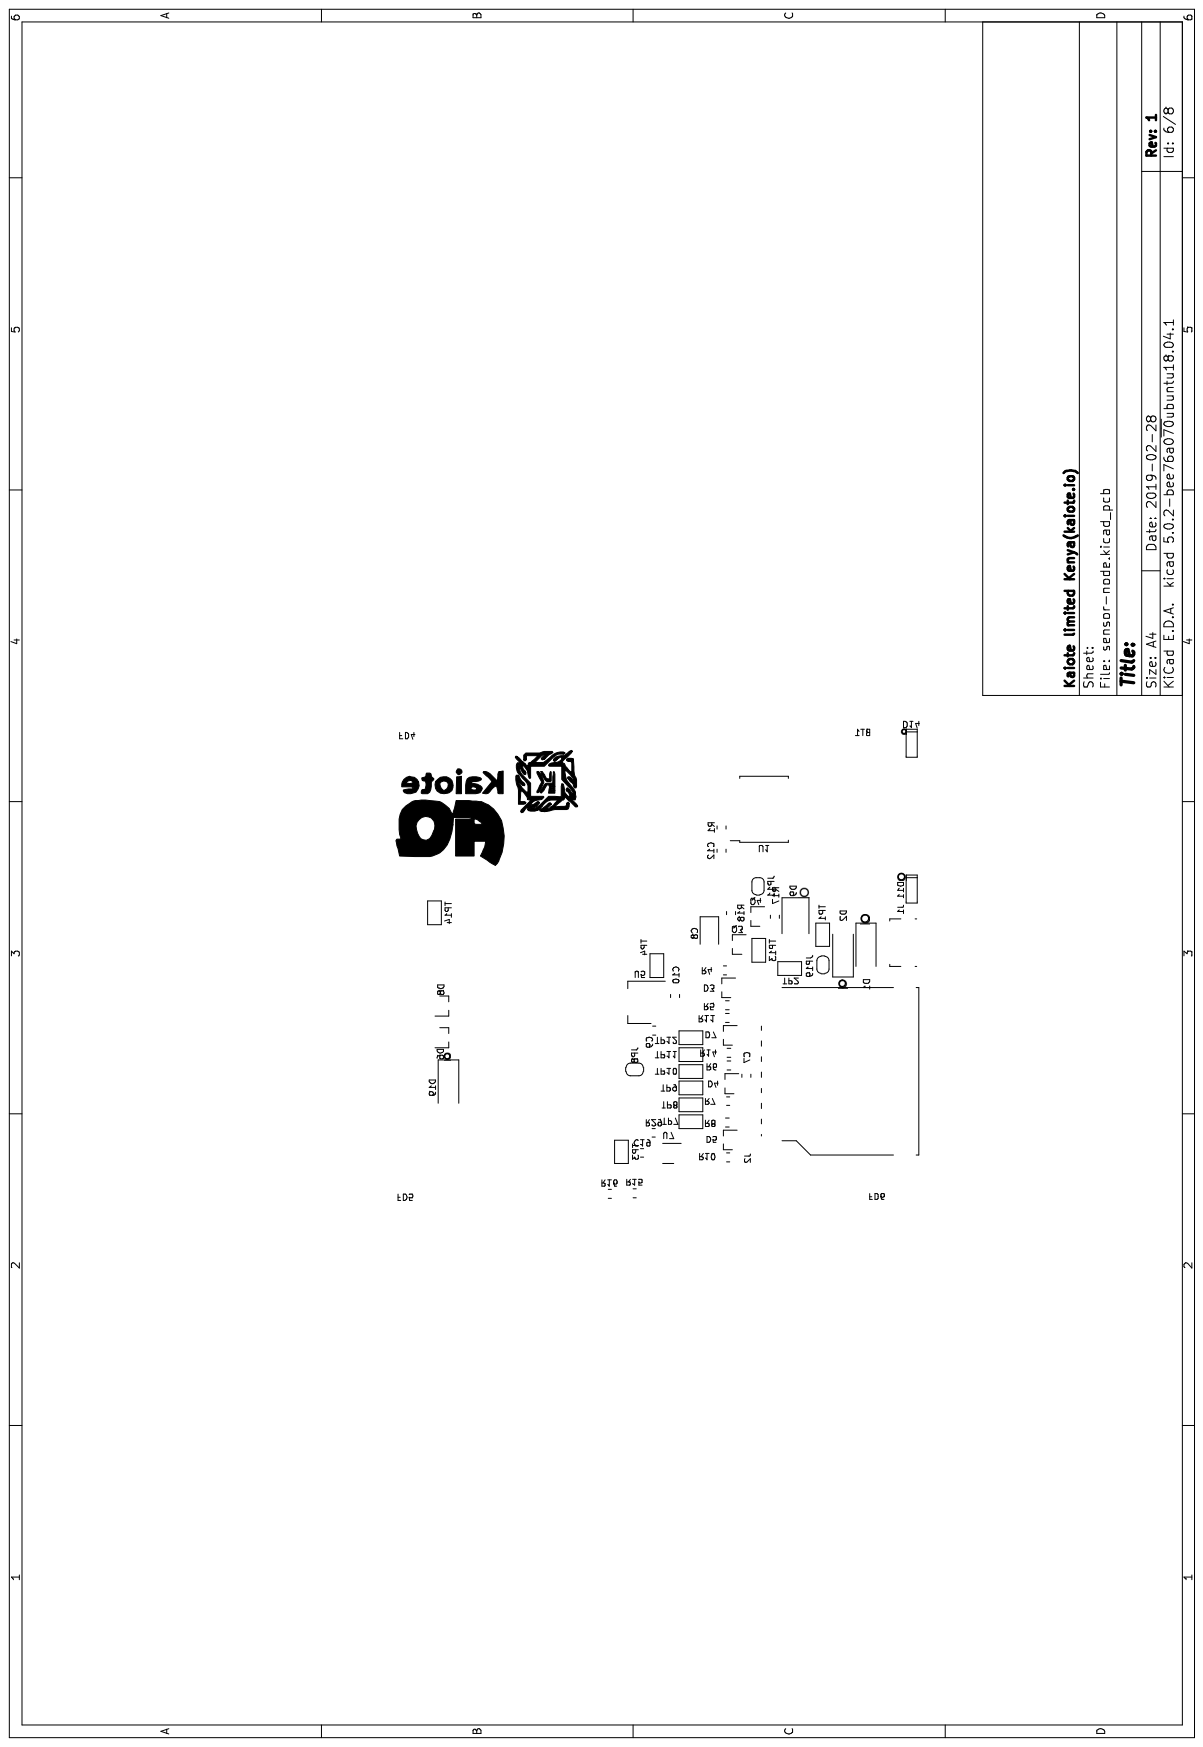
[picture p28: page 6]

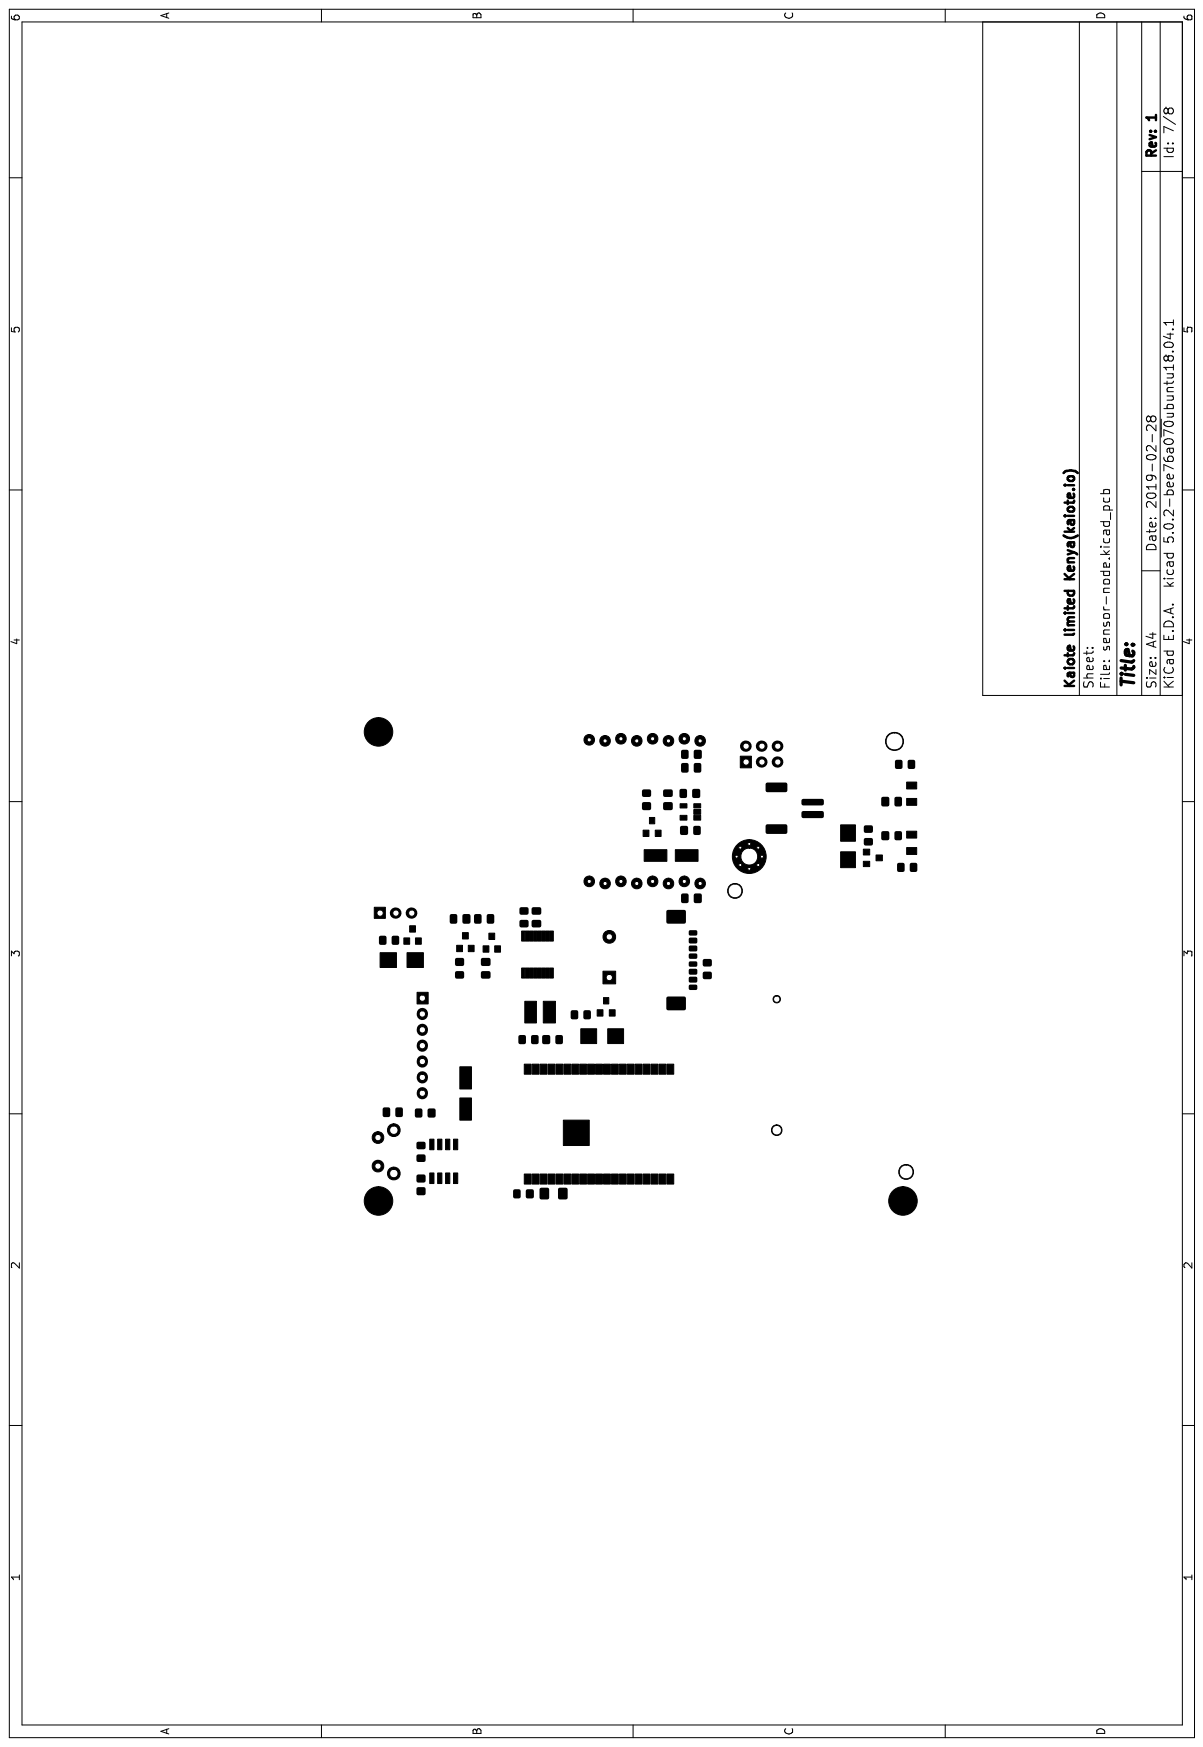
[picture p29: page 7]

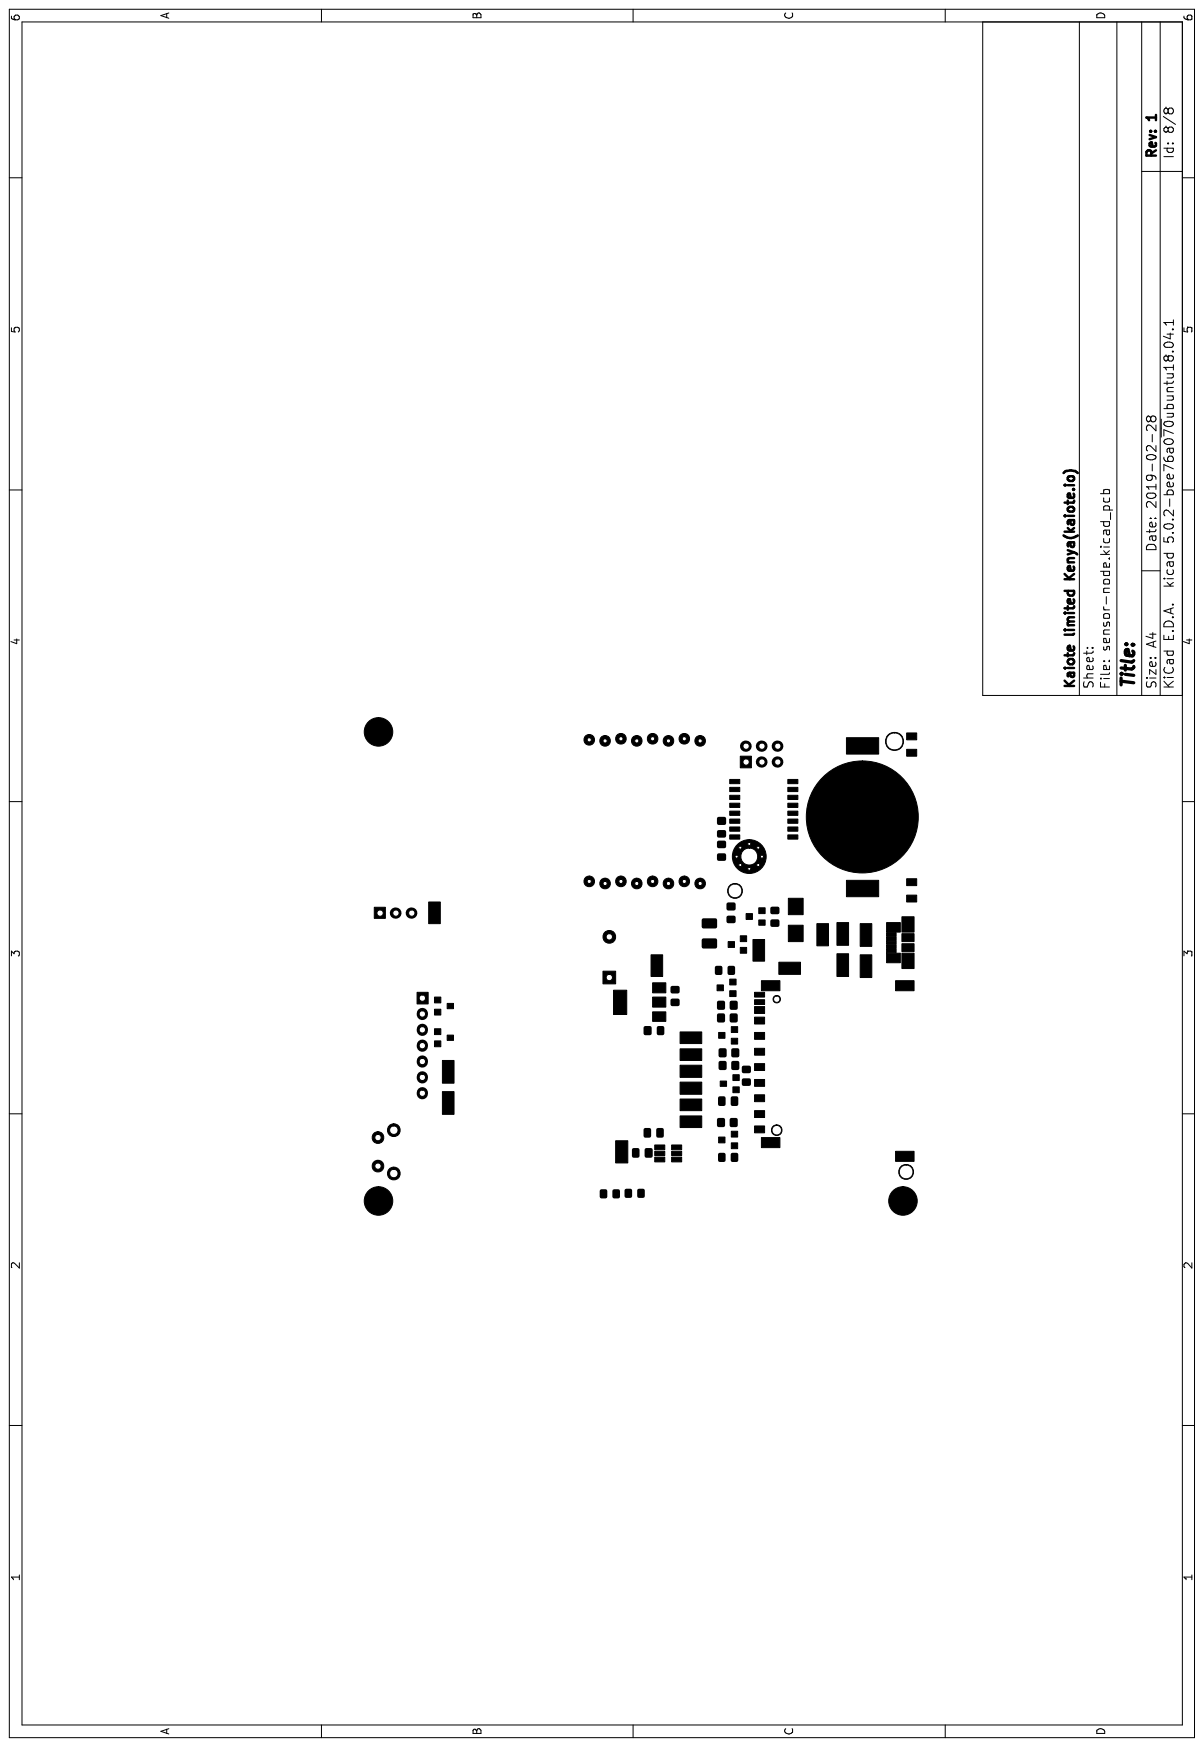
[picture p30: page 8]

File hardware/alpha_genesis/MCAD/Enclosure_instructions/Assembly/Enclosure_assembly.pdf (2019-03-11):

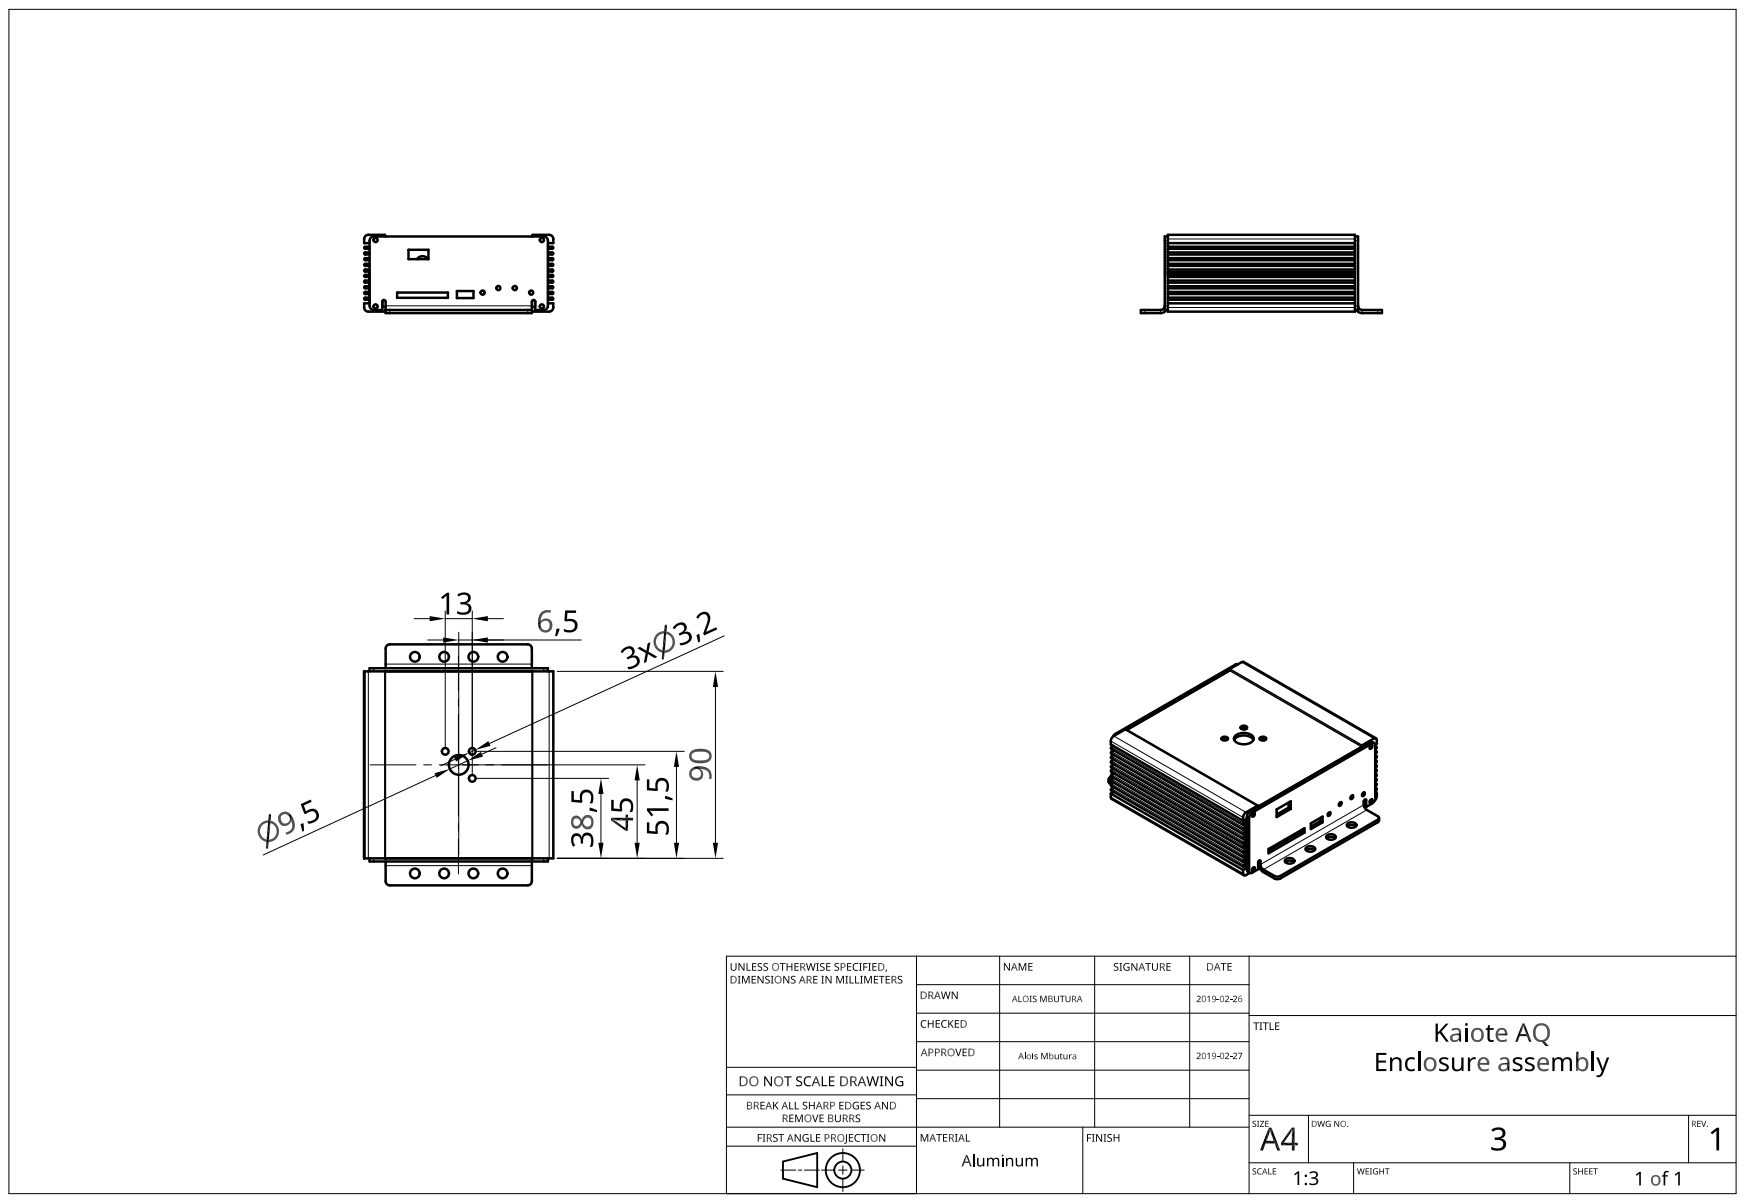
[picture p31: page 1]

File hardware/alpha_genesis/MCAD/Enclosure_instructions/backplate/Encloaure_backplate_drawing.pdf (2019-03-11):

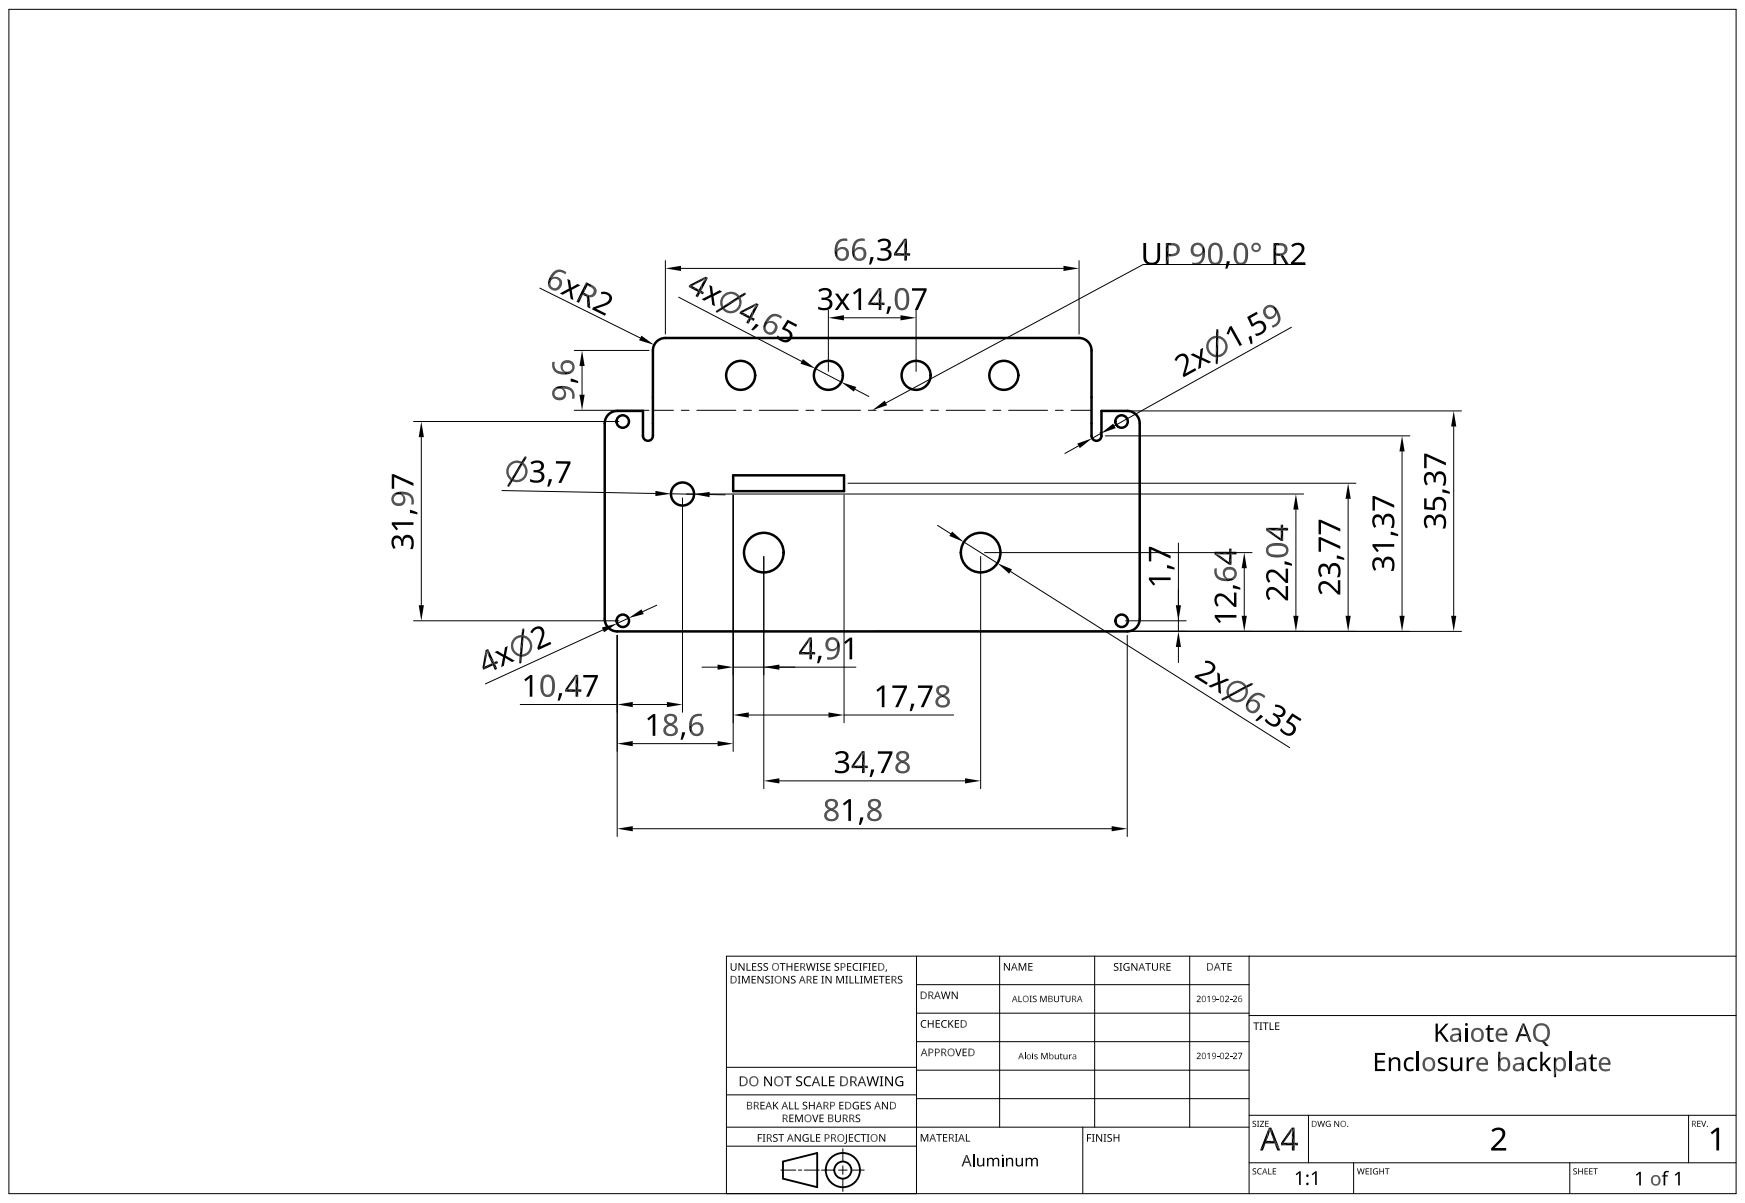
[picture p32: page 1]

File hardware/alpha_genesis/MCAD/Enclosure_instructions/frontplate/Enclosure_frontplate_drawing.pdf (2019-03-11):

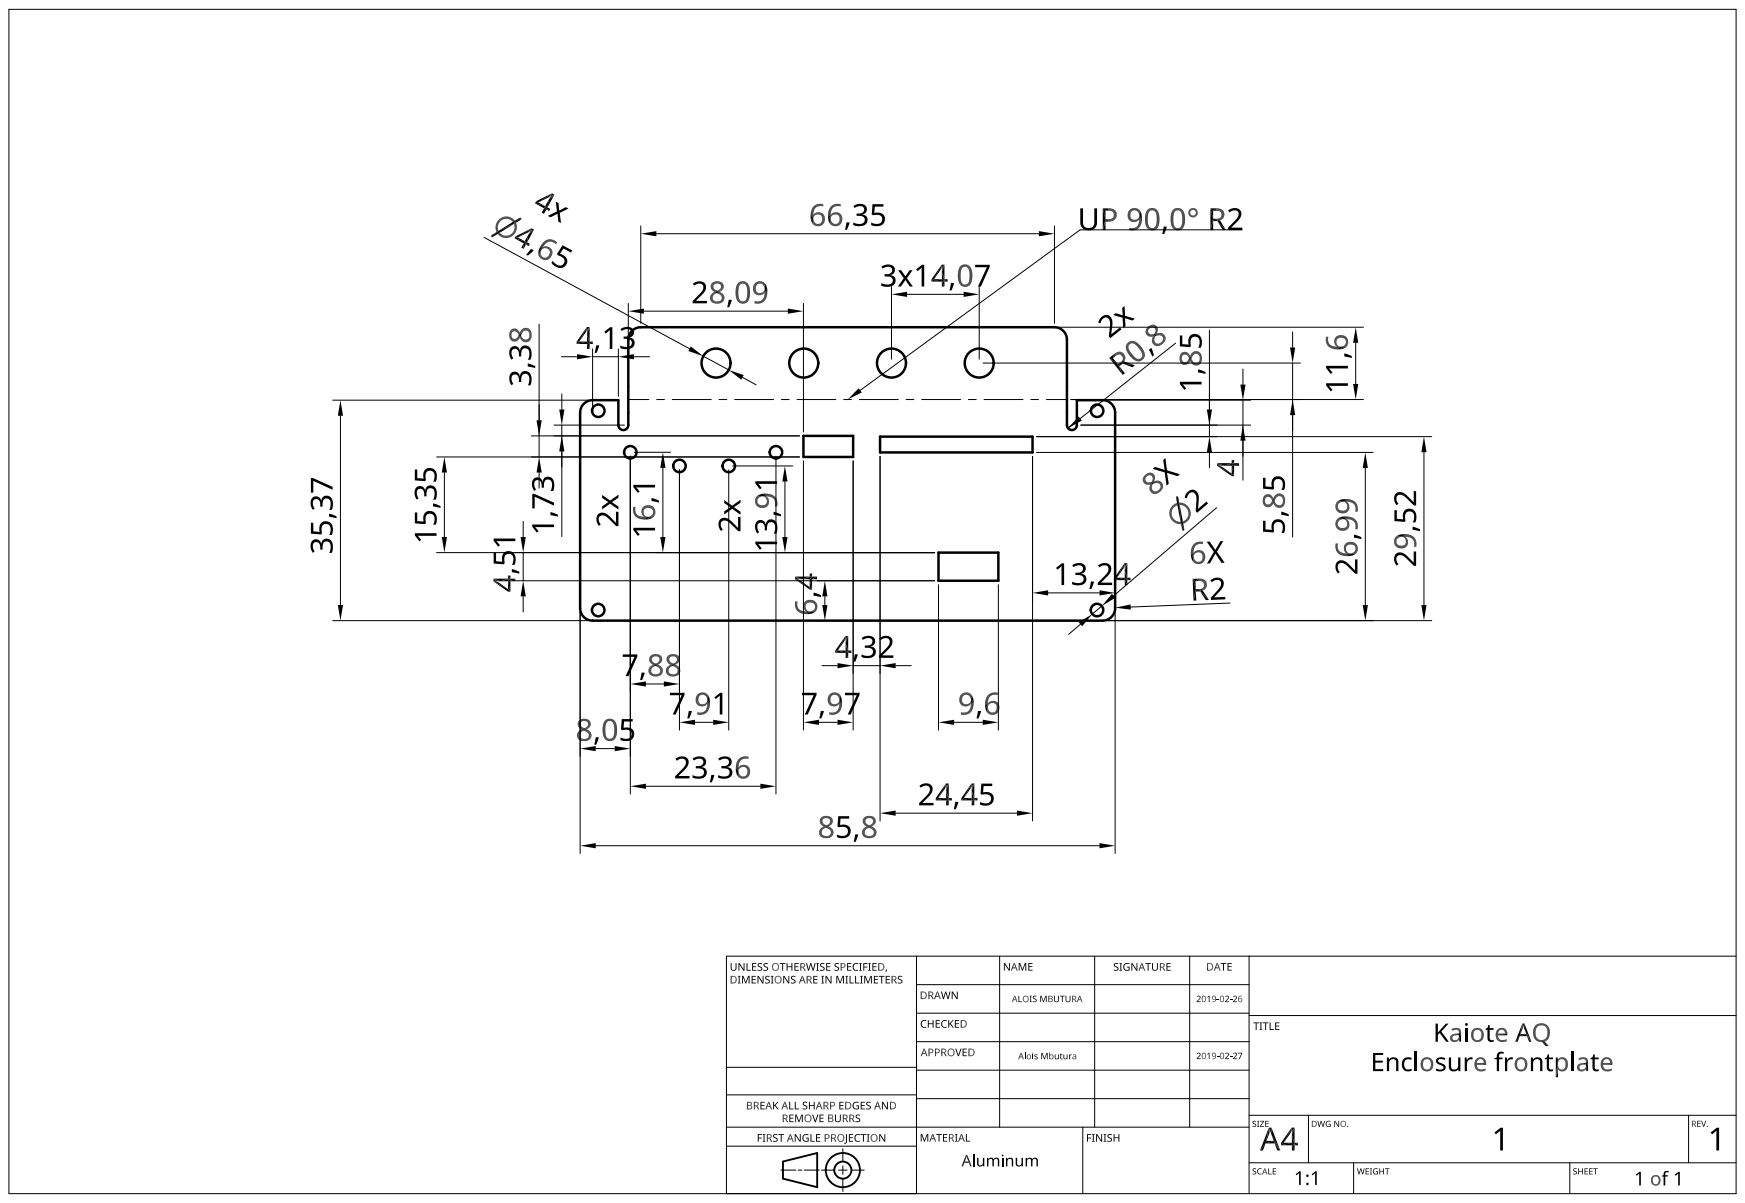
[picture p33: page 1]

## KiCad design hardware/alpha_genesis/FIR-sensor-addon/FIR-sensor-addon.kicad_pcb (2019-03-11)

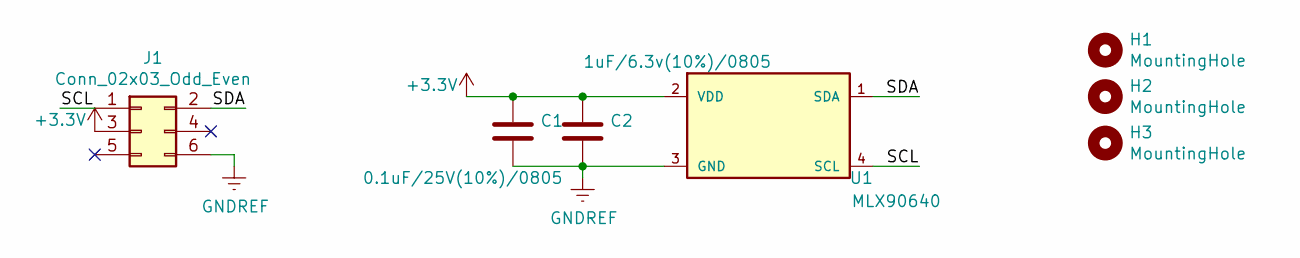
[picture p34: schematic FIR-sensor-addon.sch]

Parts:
C1: 0.1uF/25V(10%)/0805; C_0805_2012Metric_Pad1.15x1.40mm_HandSolder
C2: 1uF/6.3v(10%)/0805; C_0805_2012Metric_Pad1.15x1.40mm_HandSolder
H1: MountingHole; MountingHole_3.2mm_M3
H2, H3: MountingHole; MountingHole_2.2mm_M2
J1: Conn_02x03_Odd_Even; PinHeader_2x03_P2.54mm_Vertical
U1: MLX90640

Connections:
+3V3: C1.1, C2.1, J1.3, U1.2 (VDD)
/SCL: J1.1, U1.4 (SCL)
/SDA: J1.2, U1.1 (SDA)
GNDREF: C1.2, C2.2, J1.6, U1.3 (GND)

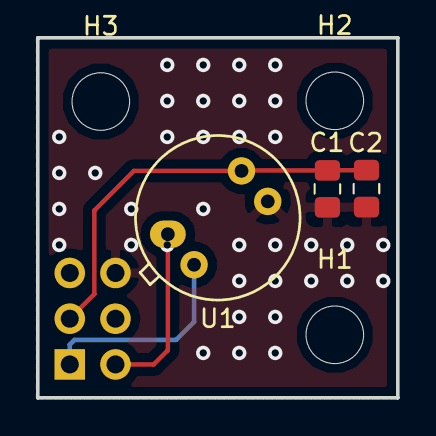
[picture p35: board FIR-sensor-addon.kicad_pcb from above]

Board: 2 copper layers, 20.0 x 20.0 mm, 7 parts (1 on the bottom side), 4 nets.

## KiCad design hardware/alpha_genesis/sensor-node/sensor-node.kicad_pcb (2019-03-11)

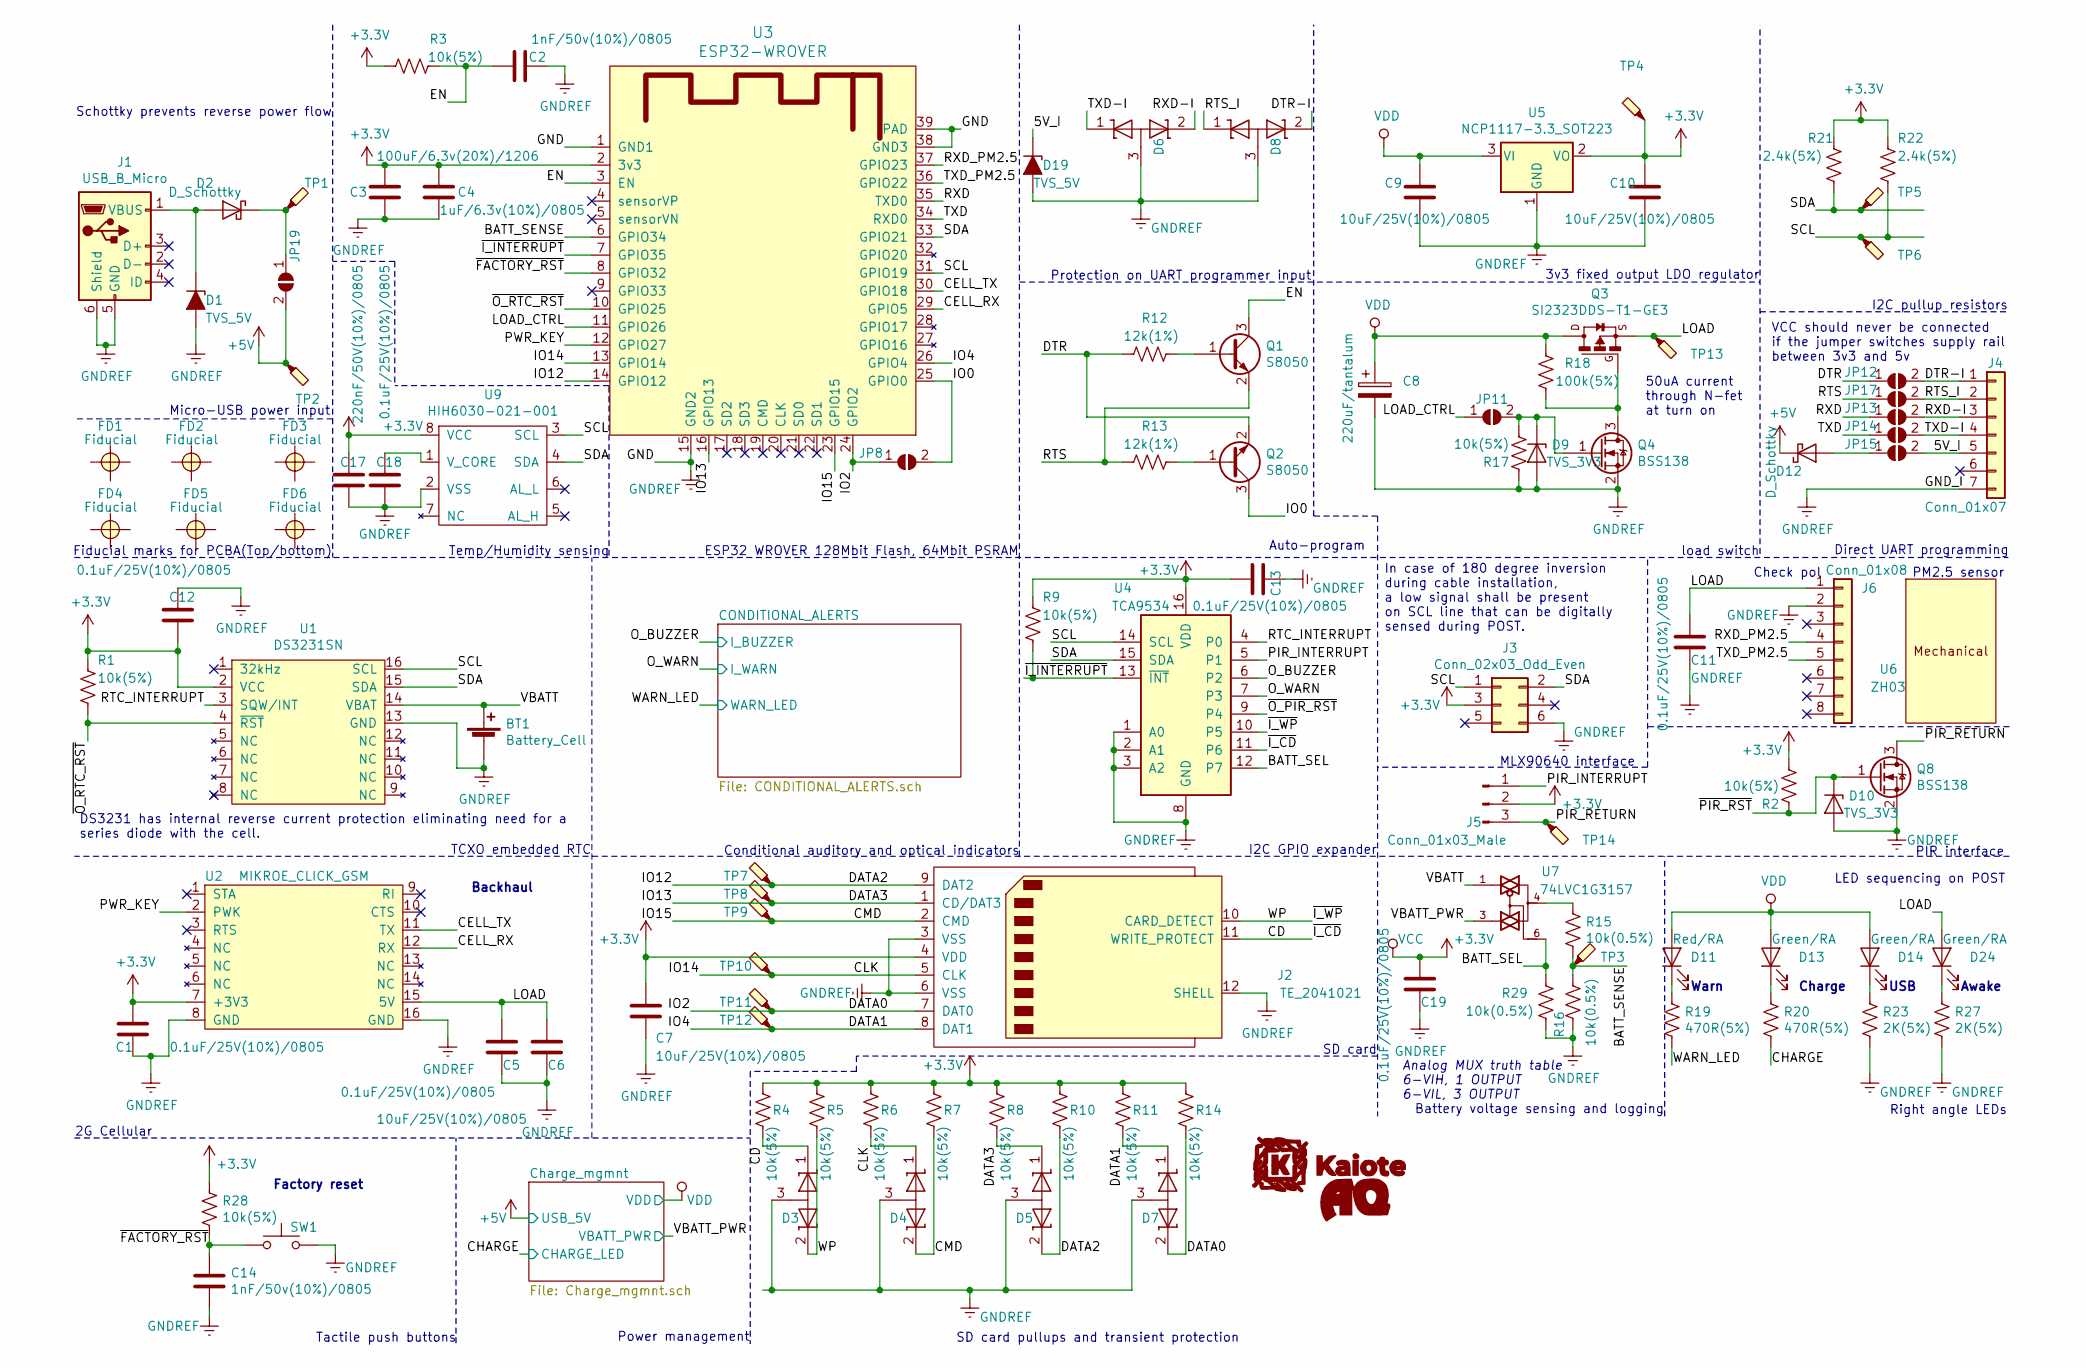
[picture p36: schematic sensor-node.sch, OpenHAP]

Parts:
BT1: Battery_Cell; BAT-HLD-001-xx-OTL
C1, C5, C11, C12, C13, C18, C19: 0.1uF/25V(10%)/0805; C_0805_2012Metric_Pad1.15x1.40mm_HandSolder
C2, C14: 1nF/50v(10%)/0805; C_0805_2012Metric_Pad1.15x1.40mm_HandSolder
C3: 100uF/6.3v(20%)/1206; C_1206_3216Metric_Pad1.42x1.75mm_HandSolder
C4: 1uF/6.3v(10%)/0805; C_0805_2012Metric_Pad1.15x1.40mm_HandSolder
C6, C7, C9, C10: 10uF/25V(10%)/0805; C_0805_2012Metric_Pad1.15x1.40mm_HandSolder
C8: 220uF/tantalum; CP_EIA-3528-15_AVX-H_Pad1.50x2.35mm_HandSolder
C17: 220nF/50V(10%)/0805; C_0805_2012Metric_Pad1.15x1.40mm_HandSolder
D1, D19: TVS_5V; D_SMA_Handsoldering
D2, D12: D_Schottky; D_SMA_Handsoldering
D3, D4, D5, D6, D7, D8: CDSOT23-T03C; SOT-23
D9, D10: TVS_3V3; D_SMB
D11: Red/RA; APA2106SRCPRV
D13, D14, D24: Green/RA; APA2106SRCPRV
FD1, FD2, FD3, FD4, FD5, FD6: Fiducial; Fiducial_classic_Small_CopperBottom_Type1
J1: USB_B_Micro; USB_Micro-B_Molex_47346-0001
J2: TE_2041021; SD_TE_2041021
J3: Conn_02x03_Odd_Even; PinHeader_2x03_P2.54mm_Vertical
J4: Conn_01x07; PinSocket_1x07_P2.54mm_Horizontal
J5: Conn_01x03_Male; PinHeader_1x03_P2.54mm_Vertical
J6: Conn_01x08; Molex_PicoBlade_53398-0871_1x08-1MP_P1.25mm_Vertical
JP8, JP11, JP12, JP13, JP14, JP15, JP17, JP19: SolderJumper_2_Open; SolderJumper-2_P1.3mm_Open_RoundedPad1.0x1.5mm
LOGO1: kaiote_logo; pcb-logo
LOGO2: AQ_logo; AQ
Q1, Q2: S8050; SOT-23
Q3: SI2323DDS-T1-GE3; SOT-23
Q4, Q8: BSS138; SOT-23
R1, R2, R3, R4, R5, R6, R7, R8, R9, R10, R11, R14, R17, R28: 10k(5%); R_0805_2012Metric_Pad1.15x1.40mm_HandSolder
R12, R13: 12k(1%); R_0805_2012Metric_Pad1.15x1.40mm_HandSolder
R15, R16, R29: 10k(0.5%); R_0805_2012Metric_Pad1.15x1.40mm_HandSolder
R18: 100k(5%); R_0805_2012Metric_Pad1.15x1.40mm_HandSolder
R19, R20: 470R(5%); R_0805_2012Metric_Pad1.15x1.40mm_HandSolder
R21, R22: 2.4k(5%); R_0805_2012Metric_Pad1.15x1.40mm_HandSolder
R23, R27: 2K(5%); R_0805_2012Metric_Pad1.15x1.40mm_HandSolder
SW1: E-switch TL1105VF160Q
TP1, TP2, TP3, TP4, TP5, TP6, TP7, TP8, TP9, TP10, TP11, TP12, TP13, TP14: TestPoint_Keystone_5015_Micro-Minature
U1: DS3231SN; SOIC-16W_7.5x10.3mm_P1.27mm
U2: MIKROE_CLICK_GSM; MIKROE_CLICK
U3: ESP32-WROVER; XCVR_ESP32-WROVER-I
U4: TCA9534; TSSOP-16_4.4x5mm_P0.65mm
U5: NCP1117-3.3_SOT223; SOT-223-3_TabPin2
U6: ZH03; KAIOTE_ZH03B
U7: 74LVC1G3157; SOT-23-6_Handsoldering
U9: HIH6030-021-001; SOIC-8_3.9x4.9mm_P1.27mm

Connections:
+3V3: C1.1, C3.1, C4.1, C7.1, C10.1, C12.1, C13.1, C17.2, C19.1, J2.4 (VDD), J3.3, J5.2, R1.1, R2.2, R3.1, R4.1, R5.1, R6.1, R7.1, R8.1, R9.1, R10.1, R11.1, R14.1, R21.1, R22.1, R28.1, TP4.1, U1.2 (VCC), U2.7 (+3V3), U3.2 (3v3), U4.16 (VDD), U5.2 (VO), U7.5 (VCC), U9.8 (VCC)
+5V: D12.1 (K), JP19.2 (B), TP2.1; also elsewhere on the board
/5V_I: D19.1 (K), J4.5, JP15.2 (B)
/BATT_SEL: R29.1, U4.12 (P7), U7.6
/BATT_SENSE: R15.2, R16.1, TP3.1, U3.6 (GPIO34)
/CD: D3.1 (K), J2.11 (WRITE_PROTECT), R4.2, U4.11 (P6)
/CELL_RX: U2.12 (RX), U3.29 (GPIO5)
/CELL_TX: U2.11 (TX), U3.30 (GPIO18)
/CHARGE: R20.2; also elsewhere on the board
/CLK: D4.1 (K), J2.5 (CLK), R6.2, TP10.1, U3.13 (GPIO14)
/CMD: D4.2 (K), J2.2 (CMD), R7.2, TP9.1, U3.23 (GPIO15)
/DATA0: D7.2 (K), J2.7 (DAT0), JP8.1 (A), R14.2, TP11.1, U3.24 (GPIO2)
/DATA1: D7.1 (K), J2.8 (DAT1), R11.2, TP12.1, U3.26 (GPIO4)
/DATA2: D5.2 (K), J2.9 (DAT2), R10.2, TP7.1, U3.14 (GPIO12)
/DATA3: D5.1 (K), J2.1 (CD/DAT3), R8.2, TP8.1, U3.16 (GPIO13)
/DTR: JP12.1 (A), Q2.2 (E), R12.2
/DTR-I: D8.2 (K), J4.1, JP12.2 (B)
/EN: C2.1, Q1.3 (C), R3.2, U3.3 (EN)
/IO0: JP8.2 (B), Q2.3 (C), U3.25 (GPIO0)
/LOAD: C5.1, C6.1, C11.1, D24.2 (A), J6.1, Q3.2 (S), TP13.1, U2.15 (5V)
/LOAD_CTRL: JP11.1 (A), U3.11 (GPIO26)
/O_BUZZER: U4.6 (P2); also elsewhere on the board
/O_WARN: U4.7 (P3); also elsewhere on the board
/PIR_INTERRUPT: J5.1, U4.5 (P1)
/PIR_RETURN: J5.3, Q8.3 (D), TP14.1
/PWR_KEY: U2.2 (PWK), U3.12 (GPIO27)
/RTC_INTERRUPT: U1.3 (SQW/INT), U4.4 (P0)
/RTS: JP17.1 (A), Q1.2 (E), R13.2
/RTS_I: D8.1 (K), J4.2, JP17.2 (B)
/RXD: JP13.1 (A), U3.35 (TXD0)
/RXD-I: D6.2 (K), J4.3, JP13.2 (B)
/RXD_PM2.5: J6.4, U3.37 (GPIO23)
/SCL: J3.1, R22.2, TP6.1, U1.16 (SCL), U3.31 (GPIO19), U4.14 (SCL), U9.3 (SCL)
/SDA: J3.2, R21.2, TP5.1, U1.15 (SDA), U3.33 (GPIO21), U4.15 (SDA), U9.4 (SDA)
/TXD: JP14.1 (A), U3.34 (RXD0)
/TXD-I: D6.1 (K), J4.4, JP14.2 (B)
/TXD_PM2.5: J6.5, U3.36 (GPIO22)
/VBATT: BT1.1 (+), U1.14 (VBAT), U7.1
/VBATT_PWR: U7.3; also elsewhere on the board
/WARN_LED: R19.2; also elsewhere on the board
/WP: D3.2 (K), J2.10 (CARD_DETECT), R5.2, U4.10 (P5)
/~FACTORY_RST: C14.1, R28.2, SW1.1, U3.8 (GPIO32)
/~I_INTERRUPT: R9.2, U3.7 (GPIO35), U4.13 (~INT~)
/~O_PIR_RST: U4.9 (P4)
/~O_RTC_RST: R1.2, U1.4 (~RST), U3.10 (GPIO25)
/~PIR_RST: D10.1 (K), Q8.1 (G), R2.1
GND: BT1.2 (-), C1.2, C2.2, C3.2, C4.2, C5.2, C6.2, C7.2, C8.2, C9.2, C10.2, C11.2, C12.2, C13.2, C14.2, C17.1, C18.1, C19.2, D1.2 (A), D3.3 (A), D4.3 (A), D5.3 (A), D6.3 (A), D7.3 (A), D8.3 (A), D9.2 (A), D10.2 (A), D19.2 (A), J1.5 (GND), J1.6 (Shield), J2.3 (VSS), J2.6 (VSS), J2.12 (SHELL), J3.6, J4.7, J6.2, Q4.2 (S), Q8.2 (S), R16.2, R17.1, R23.2, R27.2, R29.2, SW1.2, U1.13 (GND), U2.8 (GND), U2.16 (GND), U3.1 (GND1), U3.15 (GND2), U3.38 (GND3), U3.39 (PAD), U4.1 (A0), U4.2 (A1), U4.3 (A2), U4.8 (GND), U5.1 (GND), U7.2 (GND), U9.2 (VSS); also elsewhere on the board
unnamed: C18.2, U9.1 (V_CORE)
unnamed: D1.1 (K), D2.2 (A), J1.1 (VBUS)
unnamed: D2.1 (K), JP19.1 (A), TP1.1
unnamed: D9.1 (K), JP11.2 (B), Q4.1 (G), R17.2
unnamed: D11.1 (K), R19.1
unnamed: D12.2 (A), JP15.1 (A)
unnamed: D13.1 (K), R20.1
unnamed: D14.1 (K), R23.1
unnamed: D24.1 (K), R27.1
unnamed: Q1.1 (B), R12.1
unnamed: Q2.1 (B), R13.1
unnamed: Q3.1 (G), Q4.3 (D), R18.2
unnamed: R15.1, U7.4
VDD: C8.1, C9.1, D11.2 (A), D13.2 (A), D14.2 (A), Q3.3 (D), R18.1, U5.3 (VI); also elsewhere on the board

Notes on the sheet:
Right angle LEDs
PM2.5 sensor
TCXO embedded RTC
Conditional auditory and optical indicators
SD card pullups and transient protection
Battery voltage sensing and logging
Direct UART programming
VCC should never be connected if the jumper switches supply rail between 3v3 and 5v
I2C GPIO expander
Schottky prevents reverse power flow
Micro-USB power input
Auto-program
3v3 fixed output LDO regulator
50uA current through N-fet at turn on
load switch
ESP32 WROVER 128Mbit Flash, 64Mbit PSRAM
I2C pullup resistors
SD card
2G Cellular
Tactile push buttons
Protection on UART programmer input
Fiducial marks for PCBA(Top/bottom)
LED sequencing on POST
In case of 180 degree inversion during cable installation, a low signal shall be present on SCL line that can be digitally sensed during POST.
MLX90640 interface
PIR interface
Check pol
DS3231 has internal reverse current protection eliminating need for a series diode with the cell.
Awake
USB
Warn
Charge
Power management
Factory reset
Analog MUX truth table 6-VIH, 1 OUTPUT 6-VIL, 3 OUTPUT
Backhaul
Temp/Humidity sensing

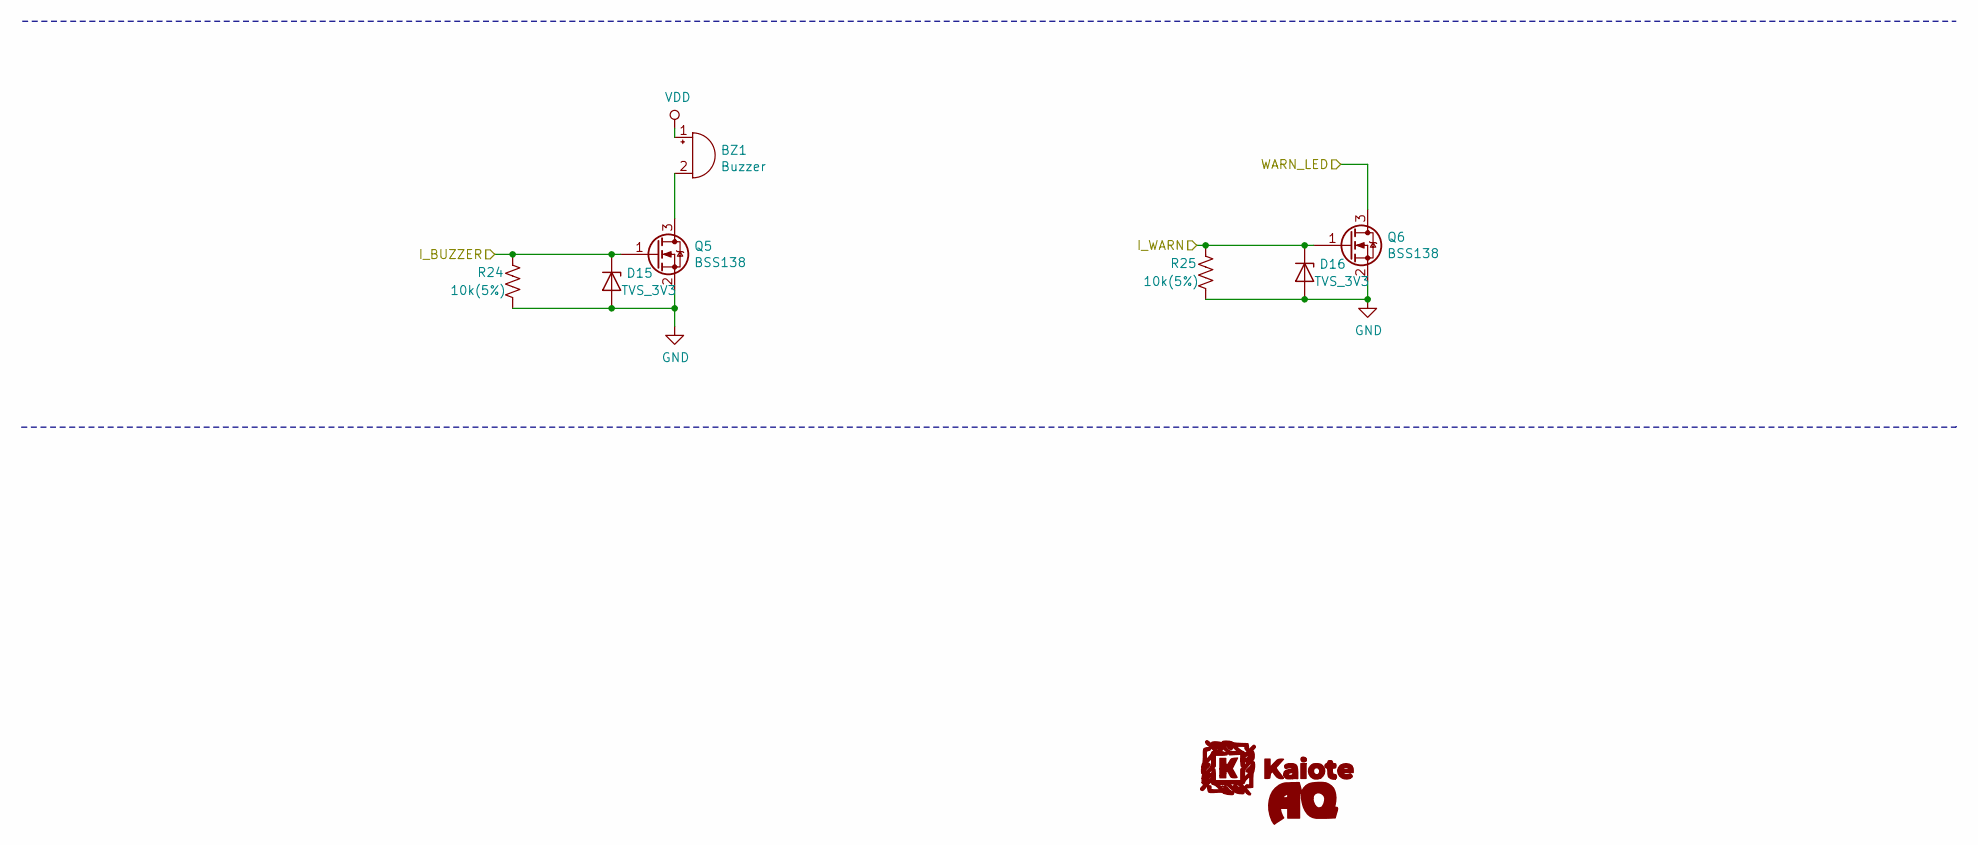
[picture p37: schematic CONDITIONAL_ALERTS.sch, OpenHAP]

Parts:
BZ1: Buzzer; Buzzer_12x9.5RM6.5
D15, D16: TVS_3V3; D_SMB
Q5, Q6: BSS138; SOT-23
R24, R25: 10k(5%); R_0805_2012Metric_Pad1.15x1.40mm_HandSolder

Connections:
/O_BUZZER: D15.1 (K), Q5.1 (G), R24.1; also elsewhere on the board
/O_WARN: D16.1 (K), Q6.1 (G), R25.1; also elsewhere on the board
/WARN_LED: Q6.3 (D); also elsewhere on the board
GND: D15.2 (A), D16.2 (A), Q5.2 (S), Q6.2 (S), R24.2, R25.2; also elsewhere on the board
unnamed: BZ1.2 (+), Q5.3 (D)
VDD: BZ1.1 (-); also elsewhere on the board

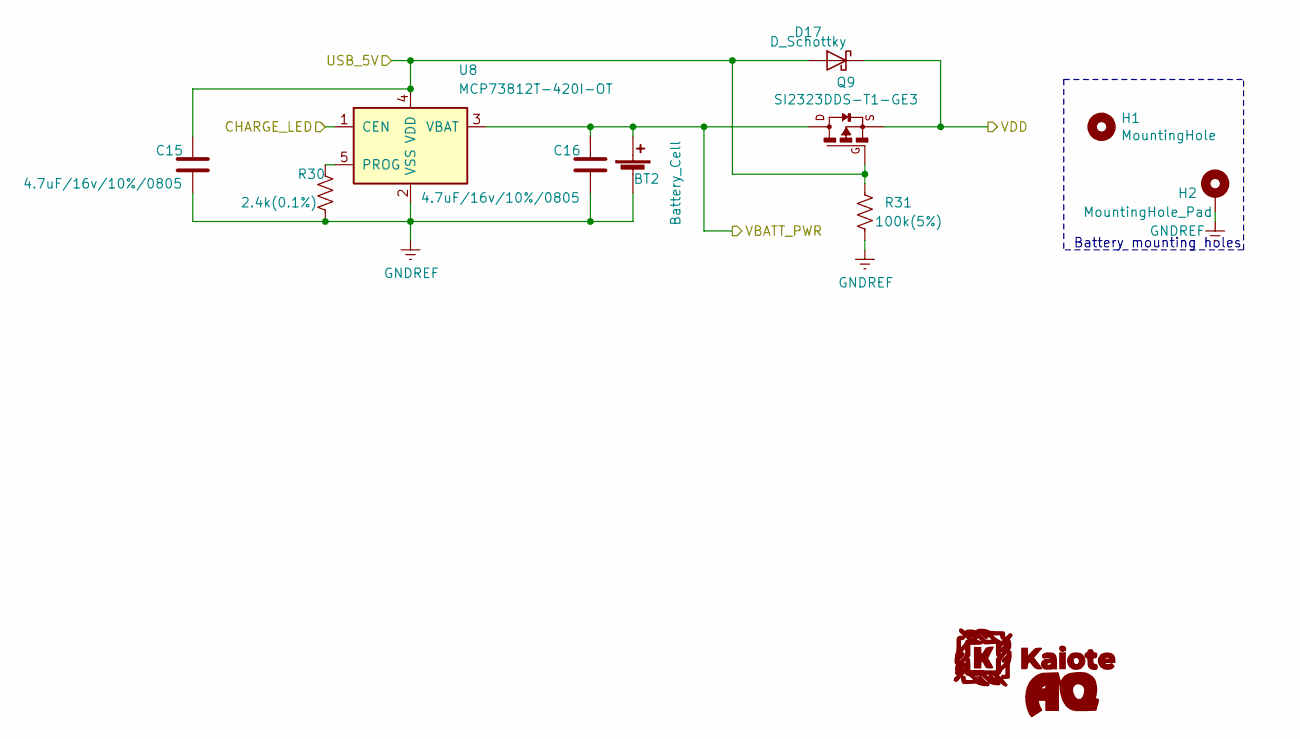
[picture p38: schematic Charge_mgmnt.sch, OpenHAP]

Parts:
BT2: Battery_Cell; JST_PH_S2B-PH-SM4-TB_1x02-1MP_P2.00mm_Horizontal
C15, C16: 4.7uF/16v/10%/0805; C_0805_2012Metric_Pad1.15x1.40mm_HandSolder
D17: D_Schottky; D_SMA_Handsoldering
H1: MountingHole; MountingHole_2.7mm_M2.5
H2: MountingHole_Pad; MountingHole_2.7mm_M2.5_Pad_Via
Q9: SI2323DDS-T1-GE3; SOT-23
R30: 2.4k(0.1%); R_0805_2012Metric_Pad1.15x1.40mm_HandSolder
R31: 100k(5%); R_0805_2012Metric_Pad1.15x1.40mm_HandSolder
U8: MCP73812T-420I-OT; SOT-23-5

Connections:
+5V: C15.1, D17.2 (A), Q9.1 (G), R31.1, U8.4 (VDD); also elsewhere on the board
/CHARGE: U8.1 (CEN); also elsewhere on the board
/VBATT_PWR: BT2.1 (+), C16.1, Q9.3 (D), U8.3 (VBAT); also elsewhere on the board
GND: BT2.2 (-), C15.2, C16.2, H2.1, R30.2, R31.2, U8.2 (VSS); also elsewhere on the board
unnamed: R30.1, U8.5 (PROG)
VDD: D17.1 (K), Q9.2 (S); also elsewhere on the board

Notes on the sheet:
Battery mounting holes

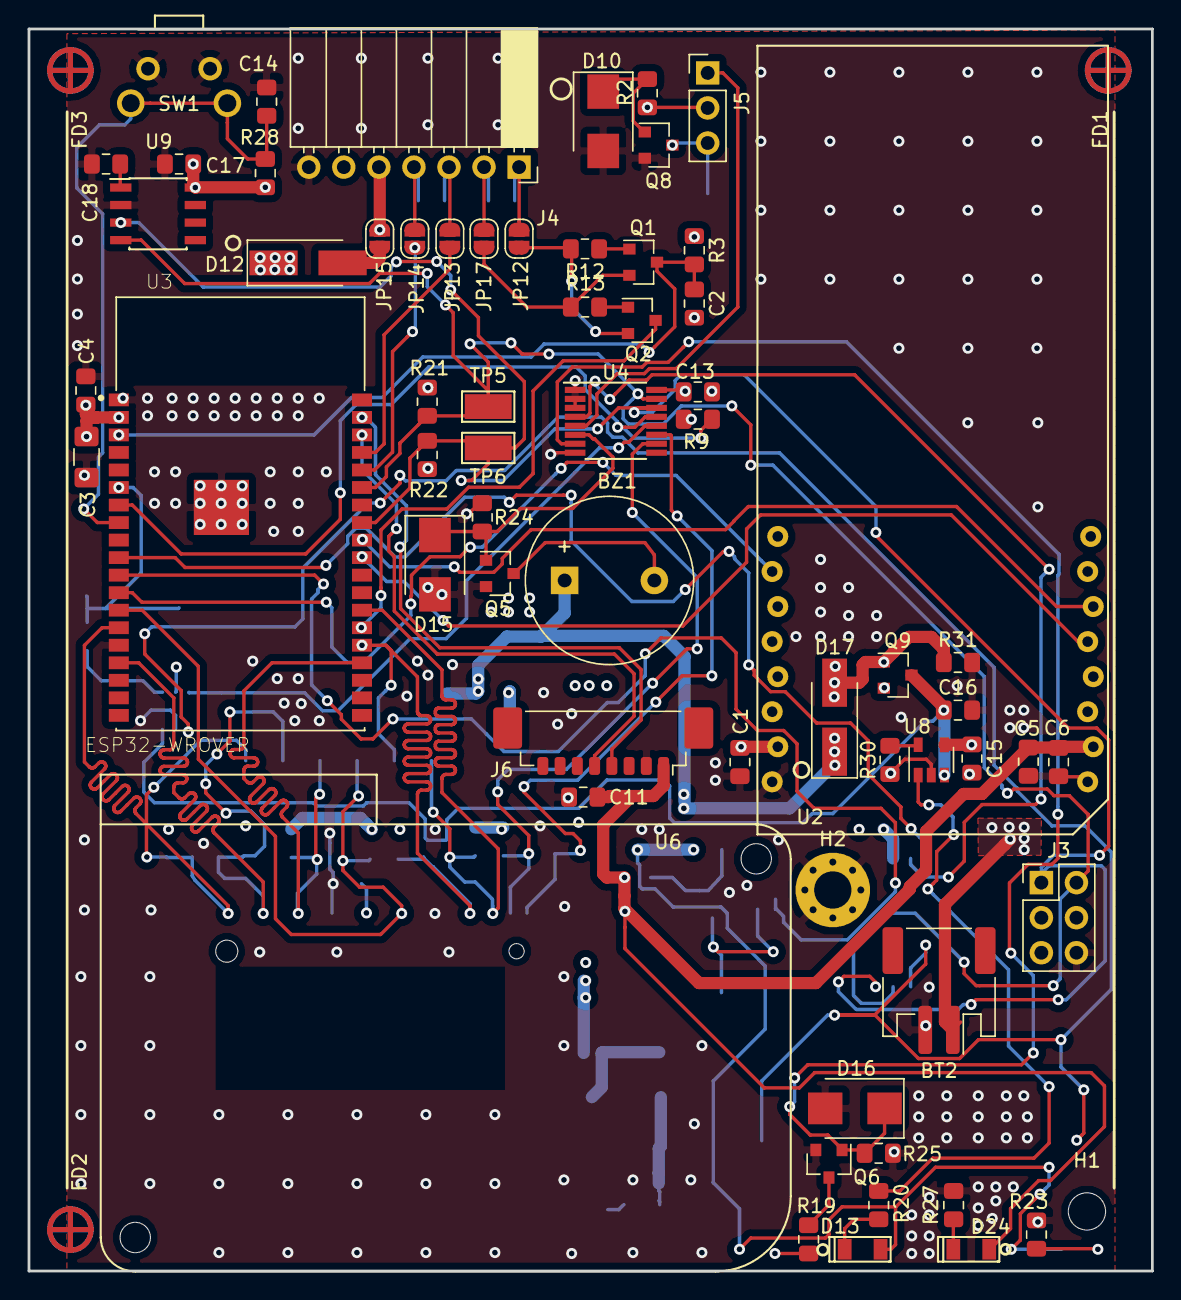
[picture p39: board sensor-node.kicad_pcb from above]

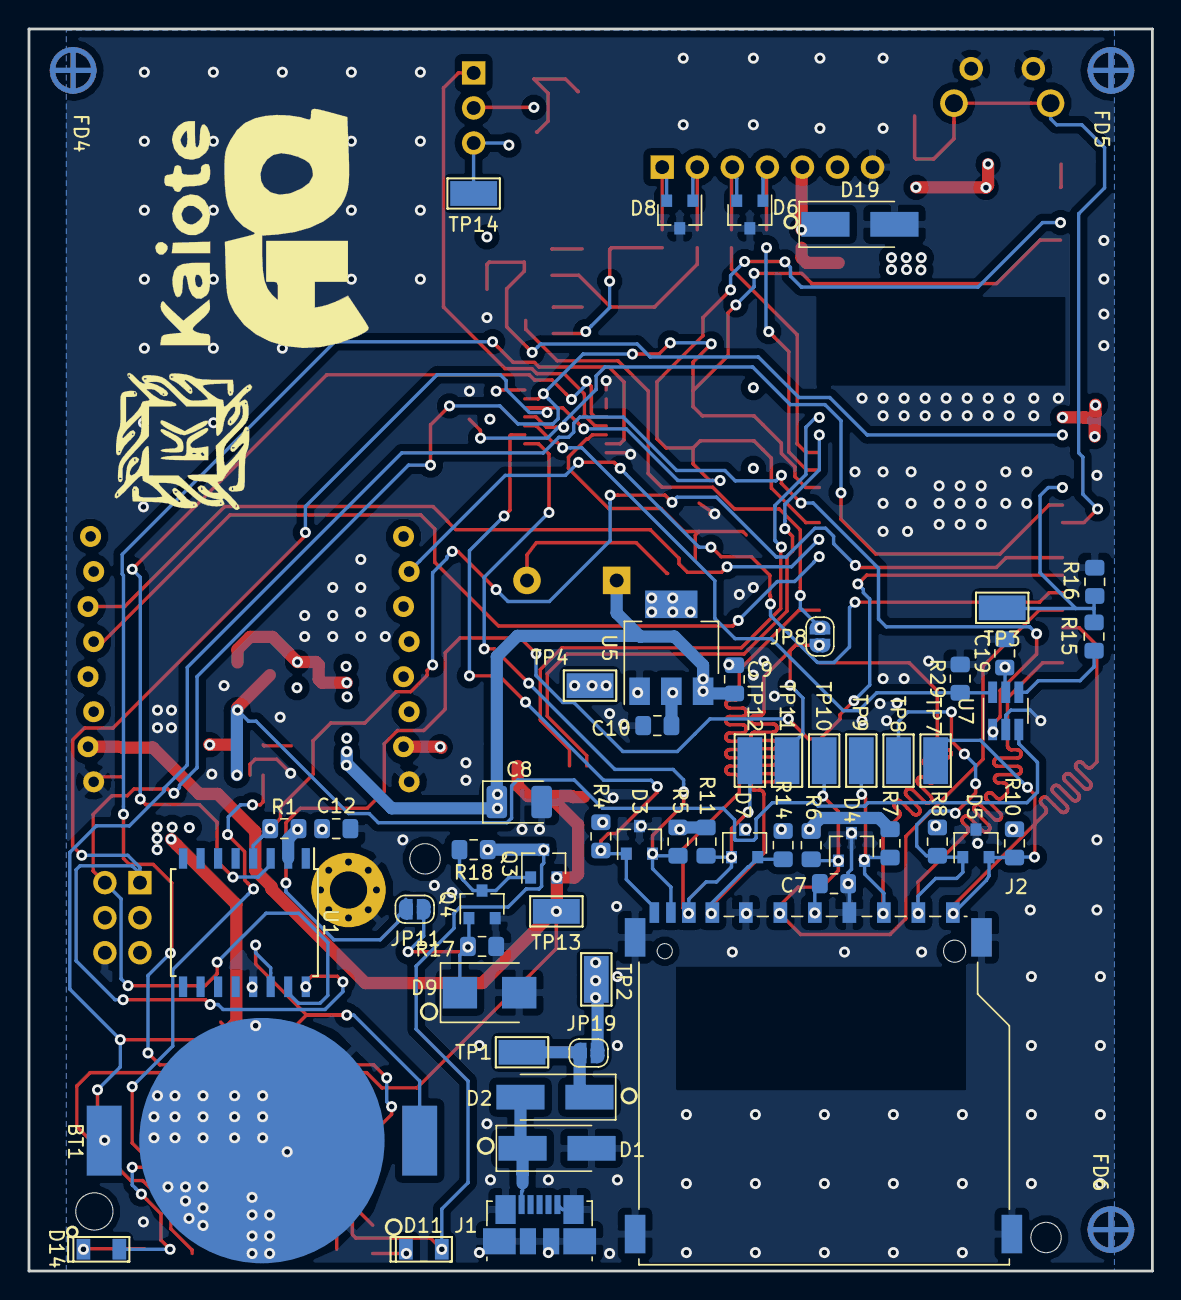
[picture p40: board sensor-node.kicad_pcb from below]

Board: 4 copper layers, 81.4 x 90.0 mm, 127 parts (60 on the bottom side), 62 nets.

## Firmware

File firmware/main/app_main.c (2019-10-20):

/*
 Author: Alois Mbutura<ambutura@eedadvisory.com>
 Copyright 2019 Kaiote.io
 Licensed under the Apache License, Version 2.0 (the "License");
 you may not use this file except in compliance with the License.
 You may obtain a copy of the License at

     http://www.apache.org/licenses/LICENSE-2.0

 Unless required by applicable law or agreed to in writing, software
 distributed under the License is distributed on an "AS IS" BASIS,
 WITHOUT WARRANTIES OR CONDITIONS OF ANY KIND, either express or implied.
 See the License for the specific language governing permissions and
 limitations under the License.
*/
#include <math.h>
#include <stdio.h>
#include <stdint.h>
#include <string.h>

#include "esp_system.h"
#include "esp_spi_flash.h"

#include "mbedtls/base64.h"

#include "espfs.h"
#include "espfs_image.h"
#include "libesphttpd/httpd-espfs.h"

#include <libesphttpd/esp.h>
#include "libesphttpd/httpd.h"
#include "libesphttpd/cgiwifi.h"
#include "libesphttpd/cgiflash.h"
#include "libesphttpd/auth.h"
#include "libesphttpd/captdns.h"
#include "libesphttpd/cgiwebsocket.h"
#include "libesphttpd/httpd-freertos.h"
#include "libesphttpd/route.h"

#include "esp_wifi.h"

#include "freertos/FreeRTOS.h"
#include "freertos/task.h"
#include "freertos/semphr.h"
#include "freertos/queue.h"

#include "freertos/event_groups.h"
#include "esp_log.h"
#include "esp_event_loop.h"

#include "nvs.h"
#include "nvs_flash.h"

#include "tcpip_adapter.h"

#include "HIH6030.h"
#include "ZH03.h"
#include "DS3231.h"
#include "TCA9534A.h"
#include <MLX90640_API.h>
#include "MLX90640_I2C_Driver.h"
#include "adc_sense.h"
#include "parson.h"
#include "user_commands.h"

#include "task_sync.h"
#include "dev_settings.h"

#include "esp_sleep.h"
#include "esp_system.h"
#include "sdkconfig.h"

#include "driver/i2c.h"
#include "driver/uart.h"

#include "esp_bt.h"
#include "esp_bt_defs.h"
#include "esp_bt_main.h"
#include "esp_gatt_defs.h"
#include "esp_gattc_api.h"
#include "esp_gap_ble_api.h"
#include "esp_eddystone_protocol.h"
#include "esp_eddystone_api.h"

#include "statistics.h"

#include <sys/unistd.h>
#include <sys/stat.h>
#include "esp_vfs_fat.h"
#include "driver/sdmmc_host.h"
#include "sdmmc_cmd.h"


#define WEB_PORT 80U
#define MAX_CONNECTIONS 12U /*Maximum tabs open...spread over all clients*/

#define GPIO_TCA9534_INT     35

#define I2C_MASTER_SCL_IO    19
#define I2C_MASTER_SDA_IO    21
#define I2C_MASTER_NUM      I2C_NUM_0
#define I2C_MASTER_FREQ_HZ  400000

#define HIH6030_ADDR        0x27
#define MLX90640_ADDR       0x33
#define TCA9534_ADDR        0x38
#define DS3231_ADDR         0x68

#define ZH03_BAUDRATE       9600
#define ZH03_UART_NUM       UART_NUM_1
#define ZH03_TXD_PIN        GPIO_NUM_23
#define ZH03_RXD_PIN        GPIO_NUM_22
#define ZH03_RX_BUF_SIZE    1024
#define ZH03_TX_BUF_SIZE    0

static const char *TAG = "APP-MAIN";

static char *infared_handshake_msg = "Hi, Infared websocket!";
static char *status_handshake_msg = "Hi, Status websocket!";
static char *tag_info_handshake_msg = "Hi, Tag websocket!";

static const char infared_cgi_resource_string[] = "/infared.cgi";
static const char status_cgi_resource_string[] = "/status.cgi";
static const char tag_cgi_resource_string[] = "/tag.cgi";

static nvs_handle my_handle;

static char *null_test_string = "\0";

struct tm date_time;

typedef struct
{
    HIH6030 IAQ_HIH6030;
    ZH03 IAQ_ZH03;
    TCA9534 IAQ_TCA9534;
    DS3231  IAQ_DS3231;
    MLX90640 IAQ_MLX90640;
    paramsMLX90640 MLX90640params;
} peripherals_struct;

peripherals_struct device_peripherals;

/*Main task handles*/
static TaskHandle_t xWebServerTaskHandle = NULL;
static TaskHandle_t xacquisitionTaskHandle = NULL;
/*Webserver subtask handles - 1 per page*/

static TaskHandle_t xStatusBroadcastHandle = NULL;
static TaskHandle_t xInfaredBroadcastHandle = NULL;
static TaskHandle_t xTagBroadcastHandle = NULL;

size_t FCBDB62F1727_count = 0;
int64_t FCBDB62F1727_cumsum_RSSI = 0;
float FCBDB62F1727_running_RSSI_mean = 0;

size_t F2416138F240_count = 0;
int64_t F2416138F240_cumsum_RSSI = 0;
float F2416138F240_running_RSSI_mean = 0;

typedef struct
{
    Websock* ws;
    char* command;
    union
    {
        int32_t* signed_value;
        uint32_t* unsigned_value;
        float* float_value;
        double* double_value;
    }value;
    char* uid;
    char* return_code_string;
} user_command;

/*Connection memory to be allocated from psram heap via malloc*/
static char* connectionMemory = NULL;
static HttpdFreertosInstance httpdFreertosInstance;

/* The event group allows multiple bits for each event,
   but we only care about one event - are we connected
   to the AP with an IP? */
const static int CONNECTED_BIT = BIT0;
static EventGroupHandle_t wifi_ap_event_group;

/*Task synchronisation event group*/
static EventGroupHandle_t task_sync_event_group = NULL;

/* declare static functions */
static void esp_gap_cb(esp_gap_ble_cb_event_t event, esp_ble_gap_cb_param_t *param);
static void esp_eddystone_show_inform(const esp_eddystone_result_t *res, const esp_ble_gap_cb_param_t *scan_result);

void statusPageWsBroadcastTask(void *pvParameters);
void infaredPageWsBroadcastTask(void *pvParameters);
void tagPageWsBroadcastTask(void *pvParameters);

static esp_ble_scan_params_t ble_scan_params = 
{
    .scan_type = BLE_SCAN_TYPE_PASSIVE,
    .own_addr_type = BLE_ADDR_TYPE_PUBLIC,
    .scan_filter_policy = BLE_SCAN_FILTER_ALLOW_ALL,
    /*Wifi takes over antenna time for (scan_window-scan_interval) in webserver mode, if hardware arbitration is preffered over software in menuconfig*/
    /*scan interval*0.625ms = scan interval time*/
    .scan_interval = 0x50,
    /*scan_window*0.625ms = scan window time*/
    .scan_window = 0x30,
    .scan_duplicate = BLE_SCAN_DUPLICATE_DISABLE
};

static void esp_eddystone_show_inform(const esp_eddystone_result_t *res, const esp_ble_gap_cb_param_t *scan_result)
{
    ESP_LOGD(TAG, "ENTERED FUNCTION [%s]", __func__);
    int connections;
    char mac_buffer[20];
    char* tag_info_string = NULL;
    switch (res->common.frame_type)
    {
        case EDDYSTONE_FRAME_TYPE_TLM:
        {
            ESP_LOGI(TAG, " Webserver setup mode bluetooth handler entry");
            if ((xEventGroupGetBits(task_sync_event_group) & CURRENT_MODE_ACQUISITION) != CURRENT_MODE_ACQUISITION)
            {
                sprintf(mac_buffer, "%02X%02X%02X%02X%02X%02X", scan_result->scan_rst.bda[0],
                                                                scan_result->scan_rst.bda[1],
                                                                scan_result->scan_rst.bda[2],
                                                                scan_result->scan_rst.bda[3],
                                                                scan_result->scan_rst.bda[4],
                                                                scan_result->scan_rst.bda[5]);
                JSON_Value *root_value = json_value_init_object();
                JSON_Object *root_object = json_value_get_object(root_value);
                json_object_set_number(root_object, "RSSI", scan_result->scan_rst.rssi);
                json_object_set_number(root_object, "BATT_VOLTAGE", res->inform.tlm.battery_voltage);
                json_object_set_number(root_object, "TIME", res->inform.tlm.time);
                json_object_set_string(root_object, "MAC", mac_buffer);
                tag_info_string = json_serialize_to_string(root_value);
                ESP_LOGI(TAG, "%s", tag_info_string);
                json_value_free(root_value);
                ESP_LOGI(TAG, "Tag info string length is %d bytes", strlen(tag_info_string));
                if (tag_info_string != NULL)
                {
                    connections = cgiWebsockBroadcast(&httpdFreertosInstance.httpdInstance, tag_cgi_resource_string, tag_info_string, strlen(tag_info_string), WEBSOCK_FLAG_NONE);
                    json_free_serialized_string(tag_info_string);
                    ESP_LOGD(TAG, "Broadcast sent to %d connections", connections);
                }
                else
                {
                    ESP_LOGD(TAG, " Tag info page JSON assembler returned NULL");
                }
                break;
            }
            else if((xEventGroupGetBits(task_sync_event_group) & CURRENT_MODE_ACQUISITION) == CURRENT_MODE_ACQUISITION)
            {
                ESP_LOGI(TAG, " Acquisition mode bluetooth handler entry");
                sprintf(mac_buffer, "%02X%02X%02X%02X%02X%02X", scan_result->scan_rst.bda[0],
                                                                scan_result->scan_rst.bda[1],
                                                                scan_result->scan_rst.bda[2],
                                                                scan_result->scan_rst.bda[3],
                                                                scan_result->scan_rst.bda[4],
                                                                scan_result->scan_rst.bda[5]);
                if(strcmp(mac_buffer, "FCBDB62F1727") == 0)
                {
                    ESP_LOGI(TAG, " Gotten 0xFCBDB62F1727");
                    FCBDB62F1727_count++;
                    ESP_LOGI(TAG, "FCBDB62F1727 TLM observation received, total: %d", FCBDB62F1727_count);
                    FCBDB62F1727_cumsum_RSSI += (scan_result->scan_rst.rssi);
                    ESP_LOGI(TAG, "FCBDB62F1727 TLM observation RSSI is %d dBm", scan_result->scan_rst.rssi); 
                    /*Check if count is zero to prevent a division by zero exception*/            
                    FCBDB62F1727_count ==0?(FCBDB62F1727_running_RSSI_mean = 0):(FCBDB62F1727_running_RSSI_mean = (float)FCBDB62F1727_cumsum_RSSI/FCBDB62F1727_count);
                    ESP_LOGI(TAG, "FCBDB62F1727 TLM running RSSI mean is %f dBm", FCBDB62F1727_running_RSSI_mean);  
                }
                else if(strcmp(mac_buffer, "F2416138F240") == 0)
                {
                    ESP_LOGI(TAG, " Gotten 0xF2416138F240");
                    F2416138F240_count++;
                    ESP_LOGI(TAG, "F2416138F240 TLM observation received, total: %d", F2416138F240_count);
                    F2416138F240_cumsum_RSSI += (scan_result->scan_rst.rssi);
                    ESP_LOGI(TAG, "F2416138F240 TLM observation RSSI is %d dBm", scan_result->scan_rst.rssi);
                    /*Check if count is zero to prevent a division by zero exception*/       
                    F2416138F240_count == 0? (F2416138F240_running_RSSI_mean = 0):(F2416138F240_running_RSSI_mean = (float)F2416138F240_cumsum_RSSI/F2416138F240_count);
                    ESP_LOGI(TAG, "F2416138F240 TLM running RSSI mean is %f dBm", F2416138F240_running_RSSI_mean);  
                }
                else
                {
                    ESP_LOGI(TAG, " Gotten unregistered tag %s", mac_buffer);
                }
                break;
            }
        }
        default:
        {
            ESP_LOGW(TAG, "Other frame type received");
            break;
        }
    }
}
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

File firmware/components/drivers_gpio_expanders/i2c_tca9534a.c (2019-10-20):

#include <stdlib.h>
#include <string.h>
#include "freertos/FreeRTOS.h"
#include "freertos/task.h"
#include "driver/i2c.h"
#include "freertos/queue.h"
#include "driver/gpio.h"
#include "esp_log.h"
#include "esp_system.h"
#include "i2c_tca9534a.h"

#define TCA9534A_I2C_TIMEOUT    1000
#define WRITE_BIT               I2C_MASTER_WRITE /*!< I2C master write */
#define READ_BIT                I2C_MASTER_READ  /*!< I2C master read */
#define ACK_CHECK_EN            0x1              /*!< I2C master will check ack from slave*/
#define ACK_CHECK_DIS           0x0              /*!< I2C master will not check ack from slave */
#define ACK_VAL                 0x0              /*!< I2C ack value */
#define NACK_VAL                0x1              /*!< I2C nack value */
#define LAST_NACK_VAL           0x0              /*!< I2C final nack value */
                    
static const char* TAG = "GPIO_EXPANDER_TCA9534A";

static esp_err_t tca9534a_i2c_write(const TCA9534 *tca9534a_inst, tca9534a_register_t tca9534a_reg, uint8_t data)
{
    ESP_LOGD(TAG, "ENTERED FUNCTION [%s]", __func__);

    if (tca9534a_reg > TCA9534A_CONFIG_REG || tca9534a_inst == NULL)
    {
        return ESP_ERR_INVALID_ARG;
    }

    uint8_t read_back = 0;

    i2c_cmd_handle_t i2c_cmd = i2c_cmd_link_create();
    i2c_master_start(i2c_cmd);
    i2c_master_write_byte(i2c_cmd, ((tca9534a_inst->address) << 1) | WRITE_BIT, ACK_CHECK_EN);
    i2c_master_write_byte(i2c_cmd, tca9534a_reg, ACK_CHECK_EN);
    i2c_master_write_byte(i2c_cmd, data, ACK_CHECK_EN);
    i2c_master_stop(i2c_cmd);
    xSemaphoreTake(tca9534a_inst->i2c_bus_mutex, portMAX_DELAY);
    esp_err_t ret = i2c_master_cmd_begin(tca9534a_inst->i2c_port, i2c_cmd, TCA9534A_I2C_TIMEOUT/portTICK_RATE_MS);
    xSemaphoreGive(tca9534a_inst->i2c_bus_mutex);
    i2c_cmd_link_delete(i2c_cmd);
    if (ret != ESP_OK)
    {
        return ret;
    }

    /**
     * Readback verification
     */
    if (tca9534_i2c_read(tca9534a_inst, tca9534a_reg, &read_back) != ESP_OK)
    {
        ESP_LOGE(TAG, "Error performing readback verification i2c transactions");
        return ret;
    }

    if (data != read_back)
    {
        ESP_LOGE(TAG, "Readback verification failed! Readback value is 0x%02X, expected 0x%02X", read_back, data);
        return ESP_FAIL;
    }

    ESP_LOGI(TAG, "Readback verification ok!");
    return ESP_OK;
}

static esp_err_t tca9534_i2c_read(const TCA9534 *tca9534a_inst, tca9534a_register_t tca9534a_reg, uint8_t *data)
{
    ESP_LOGD(TAG, "ENTERED FUNCTION [%s]", __func__);

    if (tca9534a_reg > TCA9534A_CONFIG_REG || tca9534a_inst == NULL)
    {
        return ESP_ERR_INVALID_ARG;
    }

    i2c_cmd_handle_t i2c_cmd = i2c_cmd_link_create();
    i2c_master_start(i2c_cmd);
    i2c_master_write_byte(i2c_cmd, ((tca9534a_inst->address) << 1) | WRITE_BIT, ACK_CHECK_EN);
    i2c_master_write_byte(i2c_cmd, tca9534a_reg, ACK_CHECK_EN);
    i2c_master_start(i2c_cmd);
    i2c_master_write_byte(i2c_cmd, ((tca9534a_inst->address) << 1) | READ_BIT, ACK_CHECK_EN);
    i2c_master_read_byte(i2c_cmd, data, I2C_MASTER_LAST_NACK);
    i2c_master_stop(i2c_cmd);
    xSemaphoreTake(tca9534a_inst->i2c_bus_mutex, portMAX_DELAY);
    esp_err_t ret = i2c_master_cmd_begin(tca9534a_inst->i2c_port, i2c_cmd, TCA9534A_I2C_TIMEOUT/portTICK_RATE_MS);
    xSemaphoreGive(tca9534a_inst->i2c_bus_mutex);
    i2c_cmd_link_delete(i2c_cmd);
    return ret;
}
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

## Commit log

2019-03-11 Add firmware and hardware design files
    [132117rp_3d_model.stp, APA2107.STEP, APAMBJ-135.STEP, APDA1806.STEP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]
2019-03-19 socket modification update
2019-04-08 heat map Update
2019-04-09 heatmap refinement
2019-04-13 Add untracked files
    [partitions.csv]
2019-04-13 Bugfix: Eliminate duplicate i2c bus mutexes
    Removed bug where each device on the bus had its own bus mutex. This led to a situation whereby the bus could be accessed at the same time leading to undefined behaviour..
2019-04-13 Bugfix: Eliminate duplicate i2c bus mutexes
    Removed bug where each device on the bus had its own bus mutex. This led to a situation whereby the bus could be accessed at the same time leading to undefined behaviour.
2019-04-14 Integrate MLX90640 thermal sensor
2019-04-19 Add Task notifications
    1. Added task notifications to allow tasks to exit cleanly when there are no clients on a page. The task is notified via an event group, deallocates its structures and deletes itself.
    2. Incorporated the ZH03 sensor and implemented a 5 element ring buffer queue between particulate matter sensor handler task and the status task.
    3. Used fix (1) above in this commit to fix bug that would show up when the client clicked on a separate tab when moving from the index page and went back. The particulate matter sensor would not wor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
2019-04-19 Display zeroed image on infared failure
    1. Added feature to display zero filled image buffer in the event of error during thermal buffer fetch from sensor.
2019-04-19 Add ws burst string broadcast function
    1. Refactored code to add utlity function for burst broadcasts of base64 encoded binary data, whose base64 length exceeds HTTPD's send buffer limit. Currently this limit is currently 2kB. The functio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
2019-04-19 Extend factory partition
    1. Extended factory partition from 3MByte to 8MByte to allow fullstack developer to use angular js for code management.
    [partitions.csv]
2019-04-23 Changed task closing sequencing on close event
    1. As we depend on the PM 2.5 values passed by value from the PM sensor handler, and its ambiguity due to the ampersand sign, we would like to complete dereferecing its reference first(If that is its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
    2. This is talked about by the comment " FreeRTOS queue will ALWAYS use copy-by-value, as that is how the queue operation is defined, the only question becomes what is the 'value' to be copied, is it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
2019-04-24 Remove async tasks nd events
    1. Removed async tasks and events such as UART and GPIO event from the I2C GPIO expander.
    2. Added features to ZH03 HAL such as QA mode, low power dormant mode.
2019-04-26 Add device current profiles
2019-04-26 Move power profiling files
2019-04-27 Add fielded firmware
    1. Add bluetooth and tag info recording functionality during data acquisition.
    2. Add current consumption profile for this specific firmware.
2019-04-27 change conflicting eventbit values
    1. Changed CURRENT_MODE_ACQUISITION eventgroup bit from being aliased to the same index as NOTIFY_ACQUISITION_WINDOW_DONE, the effect of this bug is that the CURRENT_MODE_ACQUISITION would be set whe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
2019-05-12 Add const qualifier to stats functions prototype parameters
    1. Added const as an extra layer of compile time checks against modifying values in the statistical functions.
2019-09-14 Add MLX90640 Python scripts folder
    1. Added python scripts folder to allow testing of the MLX90640. As at now the scripts plot temperature for a static thermal image but dynamically streamed images will be added.
2019-10-12 Rename DS3231 component folder to external_i2c_rtc
    1. Add max value for all enums to force compiler to keep size under 1 byte during compilation.
    2. Highlight work done on ds3231_set_time() and ds3231_get_time() in line with ESP32 nuance with SNTP vs UNIX time.
    3. Modified ds3231_set_alarm() to allow setting both alarms together in a single function call as opposed to the mutually exclusive implementation (Alarm 1 or Alarm 2) as was implemented prior.
    4. Removed repetitive calls to xSemaphoreTake() and xSemaphoreGive(), implementing this only on the lowest layer that interacted with I2C hardware.
    5. Initialise all local variables.
    6. Added sanity checks on function inputs for parameter valid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
2019-10-12 Add ds3231 i2c timeout
    1. Renamed source and header files to lower case.
    2. Minor formatting changes.
    3. Added i2c timeout and log tag as a const variable to allow the linker to set this in the .rodata section of the bin file.
2019-10-12 Forgot to stage const variables mentioned in commit #109
2019-10-13 Easier folder and src/hdr file naming scheme
    1. Changed folder naming scheme to the general device class name without including any of its characteristics, for example, i2c or uart.
    2. Changed the source and header file name of the specific device to include its characteristics that affect hardware, for example, communication protocol used, which would thus affect pin usage in h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
2019-10-13 Rename particulate matter sensor folder
2019-10-14 Commit with minor additions on PM sensor
2019-10-16 Additional changes to PM sensor code
2019-10-16 Minor corrections and additions to PM sensor codebase
2019-10-17 Prevent reading past buffer boundaries
    1. Added loop variable checks to avoid reading past buffer boundaries.
    2. Changed Particulate matter reading variable types from int32_t to uint16_t as the best of sensors can only go till 50,000 μg/m³, which is covered by the variable's 0-65535 range.
2019-10-18 Finalise particulate matter sensor src code
2019-10-18 Finalise particulate matter sensor src and hdrcode
2019-10-20 Modify onchip ADC driver
    1. Modified the onchip ADC driver to take in ADC channel, sample width and attenuation parameters from user code instead of being set statically internally.
    2. Added error checking
    3. Added ADC struct declaration in onchip_adc.h header file
2019-10-20 Change variable type name defining pin directions 1. Changed 'tca9534a_pintype_t' enum type to tca9534a_pin_direction_t 2. Removed pin polarity enum as polarity is not supported by default.
2019-10-20 Updated function prototypes parameters in header file
2019-10-20 Moved firmware folder to repo root
    [partitions.csv]
2019-10-20 Rearrange power profiling captures
2019-10-20 Add 2 sample OpenHAP data captures
    [2018-04-27-rural-kiambu.csv, 2018-05-17-urban-kibera.CSV]
2019-10-20 Rename data samples folder
    [2018-04-27-rural-kiambu.csv, 2018-05-17-urban-kibera.CSV]
2019-10-20 Remove uppercase from data filename
    [2018-05-17-urban-kibera.csv]
2019-10-20 Remove old data filename from repo
    [2018-05-17-urban-kibera.CSV]
2019-10-20 Correct year of datafile capture from 2018 to 2019
    [2019-04-27-rural-kiambu.csv, 2019-05-17-urban-kibera.csv]
2019-10-21 capture all changes in hardware design files
    [CONDITIONAL_ALERTS.sch, Charge_mgmnt.sch]
2019-10-21 Move hardware associated files
    [132117rp_3d_model.stp, APA2107.STEP, APAMBJ-135.STEP, APDA1806.STEP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]
2019-10-21 Add sample results to readme
2019-10-22 Change hardware version naming
    [132117rp_3d_model.stp, APA2107.STEP, APAMBJ-135.STEP, APDA1806.STEP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]
2019-10-22 Add README in samples folder
2019-10-23 Rename samples folder for clarity
    [2019-04-27-rural-kiambu.csv, 2019-05-17-urban-kibera.csv]
2019-10-23 Minor rename
    [2019-04-27-rural-kiambu.csv, 2019-05-17-urban-kibera.csv]
2019-10-23 Update data samples README
    Included description of some fields present in the data sheets
2019-10-23 Add temperature snapshot data
2019-10-26 Added power consumption to README
2019-10-26 Cropped power consumption graph
2021-05-19 Update vscode IDE settings
    1. Updated VS code C/C++ intellisense lint settings to support the
    Xtensa ESP32 C++ compiler. The lint tool will parse code in accordance
    with C++14 rules.
    2. The base search paths were also modularised and placed within
    their own variables. Added search paths include compiler search
    path, project search path, workspace search path and standard
    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
